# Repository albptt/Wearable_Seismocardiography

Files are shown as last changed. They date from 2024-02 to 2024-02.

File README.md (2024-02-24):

<h1 align="center"> HEA </h1>

<p align="center">
  animated
</p>

   <br> 
   <br> 
   
## Getting Started
### Clone the repository
Run the command on your terminal at the desired location:
```
git clone git@github.com:ltebs-polimi/AY2324_I_Project-6.git
```
### Dependencies
It is recommended to create a virtual environment to run the GUI. This can be done by running on your terminal:
```
python -m virtualenv GUI_venv
```
The latest versions of these libraries should then be installed within the virtual environment:
- ```PyQt5```
- ```numpy```
- ```scipy```
- ```pandas```
- ```openpyxl```
- ```pyqtgraph```
- ```os```
- ```sys```
- ```time```
- ```logging```
- ```struct```
## Filetree
Directories are organized as follows:
```
││├───CASE
│││   └──STL files
│││
││├───GUI
│││   ├──pyqt5_venv
│││   └──GUI.py
│││
││├───PCB
│││   ├──HEA.bdr
│││   └──HEA.sch
│││
││└───PSoC_code
││    ├──Oled-Psoc5
││    └──Stream mode.cydsn
││       │
││       ├───Generated_Source
││       │   └───PSoC5
││       └───TopDesign
││
│└───Validation_Study
│    ├──Output_Measurements
│    └──Plots
│
└───Images

```
   
## Intro
The aim of the present project is to develop a wearable device for the continuous monitoring of the heart rate, using the seismocardiography tecnique. 
  
### Seismocardiography
Continuous cardiac monitoring is necessary for the diagnosis of cardiovascular diseases. Medical emergencies caused by cardiac arrests can be prevented by a continuous cardiac monitoring, which can be easily provided by a wearable device. [^1]

Seismocardiography consists in the extraction of the heart rate value from the measurement of the vibration of the chest caused by the contraction of the heart, the closure of the cardiac valves and the ejection of the blood into the vascolature. [^1]  This term appeared in literature for the first time in the 90's. Vibrations induced by the cardiac activity are mainly correlated to valve closure (heart sounds) and cardiac systole. In particular, seismocardiographic movements at relatively low frequency reflect the recoil forces that results from the contraction of the heart muscle when it ejects blood into the vessels. These forces are responsible for body accelerations in the order of 5 mg. [^2]
  
Failing at reaching the same performances of other well established measurement techniques for the heart rate, seismocardiography didn't find a wide usage in the clinical practice. However, in the last 20 years, thanks to the development brought to the inertial sensors field by MEMS technology, this technique has been at the center of several studies. [^2] Appropriate sensors for seismoardiography are acceleroemeters and IMUs (6 axes accelerometer-gyroscope or 9 axes accelerometer-gyroscope-magnetometer). [^1] Studies present in literature investigated the usage of both single sensors and multiple sensors combined together, and vary in the site of measurement and type of processing utilized. 
  
With the spread of wearable devices and the lowering in their prices, it becomes important to further study the application of cheap and miniaturized sensors to perform biosignal analysis.
Accelerometers and ECG electrodes are common sensors inserted in smart garments such as T-shirts for the monitoring of the athlete performance and smart pajamas for the assessment of the quality of sleep. One of the main objectives in this field is the reduction in the number of the sensors needed to extract the wanted information. Limiting the electronics reduces both the production and the maintenance costs and simplifies the design of such garments. 

Most of the studies present in literature use just one accelerometer as sensor to study the heart rate acquisition in static conditions. Some more recent studies proposed the usage of a second accelerometer to measure the accelerations at the chest level not caused by the cardiac contraction, in order to remove motion artefacts that are superimposed to the heart signal and to make the tecnique effective even in conditions of light movement. [^3]
  
### Heart attack
The proposed solution is a device called "Heart attack" or "HEA" in short. It uses a single 3 axes accelerometer positioned on the chest in contact with the skin, connected through wires to a unit that can be worn on the belt or on the side with a shoulder strap, and that both provides a first interface with the user and manages the communication with a pc. A graphical user interface shows on a pc the result of the measurement and makes the utilizer able to connect and operate with the device. In short, the device records the data relative to the acceleration of the chest of the user and sends it to a pc that has previously been connected to the device throught the appropriate software. The processing of the raw data and the computation of the heart rate value is performed on the pc. Then, the extracted HR value is both sent back to the device, which uses it to manage the peripherals, and displayed on the pc screen both numerically and through a real-time plot. 

The initial solution aimed to incorporate the use of two accelerometers, but during the development process, it was decided to opt for a single accelerometer. This choice yielded satisfactory results while maintaining the simplicity and cost-effectiveness of the device in a hypothetical industrial context.
  
The details of the project are discussed in the following sections:
- [Hardware](#hardware)
- [Firmware](#firmware)
- [Communcation](#communication)
- [Processing](#processing)
- [Graphical user interface](#graphical-user-interface)
- [Acquisition Protocol](#acquisition-protocol) 
- [Clinical validation study](#clinical-validation-study) 
- [Limitations and future developments](#limitations-and-future-developments)

   <br> 
   
## Hardware
### Reference Folder: `PCB`, `Case_3Dprint`
  
HEA is composed by an accelerometer fixed in position on the chest of the user by a band and inserted in a protective shell, and by a central unit installed into a rigid case that can be worn on the belt, thanks to a clip, or on the side thanks to a shoulder strap.  

<br> 

<div align="center">

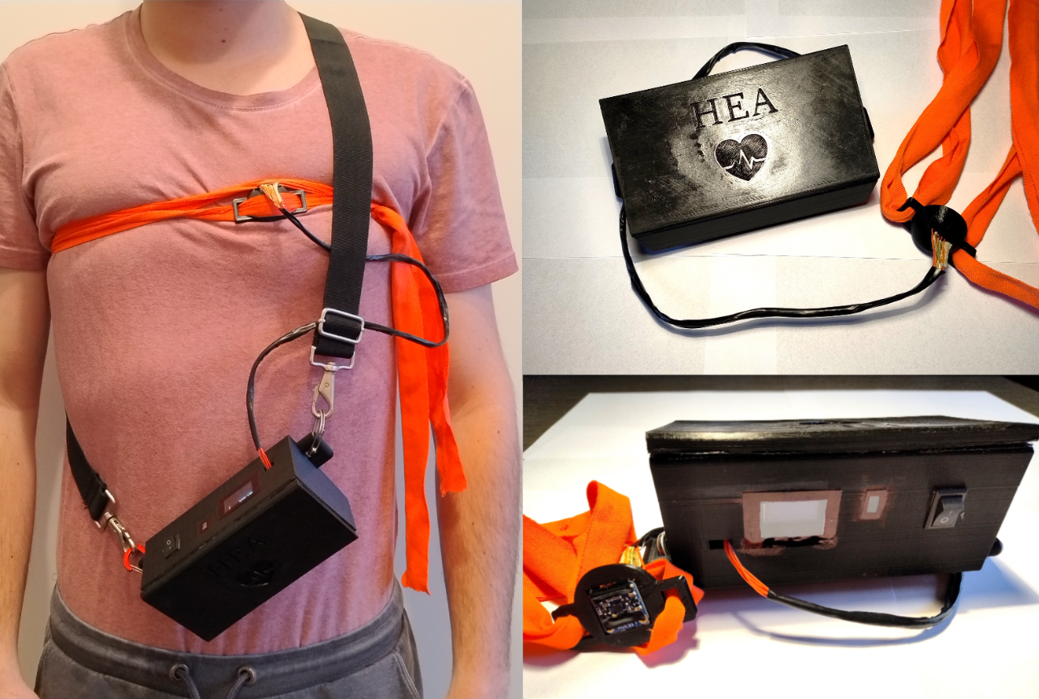
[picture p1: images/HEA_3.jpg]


</div>
  
<br>
  
The electronic circuit has been simulated in breaboard before designing the PCB.   
The electronical components used for the main module are: 
- Psoc 5LP, accelerometer LIS3DH, bluetooth module HC-O6, OLED screen ElectroPeak 0.96'', RBG led, buzzer, 9V alkaline battery, switch, linear voltage regulator LM7805, resistors (220Ω 2x, 330Ω 4x, 1KΩ 4x, 10KΩ 2x), capacitor 100μF.
  
<br>  

<div align="center">

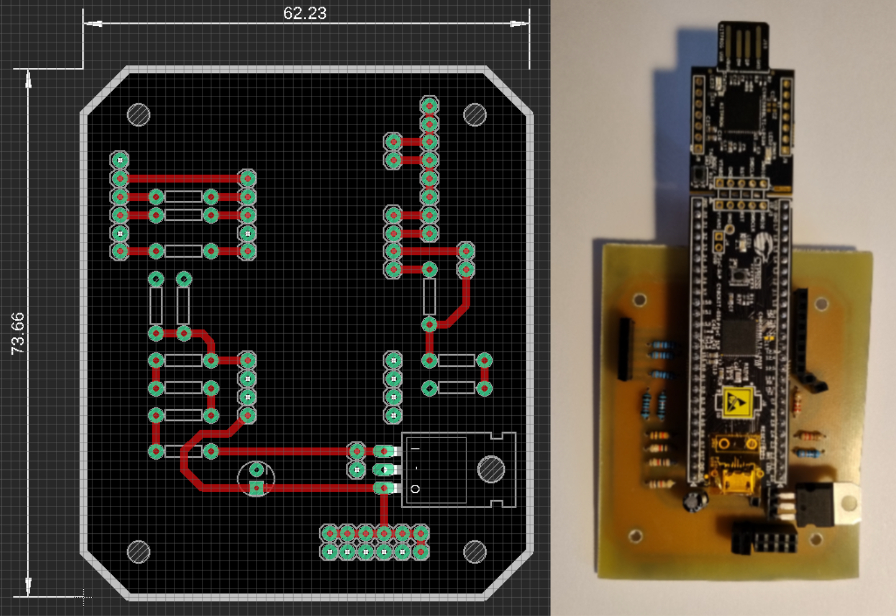
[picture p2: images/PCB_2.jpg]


</div>
  
<br>
  
A reset circuit has been added to the main module in order to automatically reset the microcontroller every time the device is turned on.
The electronical components used for the reset circuit are: 
- Dual Operational Amplifier LMx58 Low-Power, resistors (220Ω 1X, 330Ω 1X, 10KΩ 1x), capacitor 470μF.
  
<br>  

<div align="center">
  
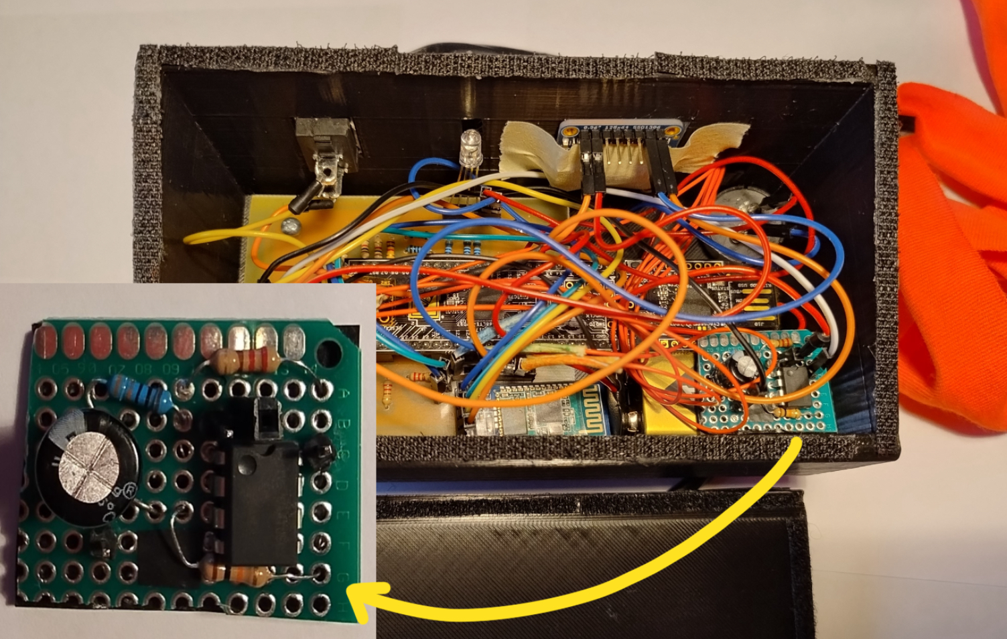
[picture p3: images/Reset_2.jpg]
Reset Circuit


</div>

 <br> 
  
### Hardware functioning discussion:
- The accelerometer and the OLED screen communicate with the microcontroller via I2C, whereas the bluetooth module communicates via UART.
- The accelerometer has also a connection between its interrupt pin and a pin of the microcontroller, so that it can trigger an interrupt when the FIFO register is full. 
- The oled screen shows the name of the device on power on. After 5 seconds it switches to a second window that shows the heart rate value and battery level over time. When the streaming is ongoing, the OLED screen is updated every 5 seconds with the new istantaneous HR value. Every hour the battery level is sampled, this event triggers also an update of the OLED screen to display the updated battery level. 
- The RGB led communicates information about the connection status of the device. If the device is not connected it flashes a red light, if the device is connected but it is not streaming data it emits a stable green light, if the device is connected and it is streaming data it emits a stable blue light. 
- The buzzer can supply information about the state of the battery and about the heart rate value via an alarm. The alarm is triggered when the heart rate value overcomes 120 bpm (which means that the user is suffering tachycardia) or when the battery goes below 5% (a new battery is needed). The alarm lasts 3 seconds, then it is disabled for 30 seconds, after which, if the triggering condition is still present, it will turn on again. 
- The PSOC 5LP and all the peripherals run on 5V, so the 9V of the battery are reduced and stabilized to 5V by the linear voltage regulator. 
- Resistors are used to limit the current running in the RGB led and to reduce the TX signal sent by the microcontroller to the bluetooth module from 5V to 3.3V, to cope with the HC-06 limitations. 
- The 100μF capacitor grants a constant power supply even in case of spikes in the current request of the circuit. 
- A voltage divider is used to reduce the 9V of the battery to 5V in a proportional way, in order to sample such signal with a pin of the microcontroller connected to an ADC and to use it as indication of the battery residual charge.
- The PCB hosts the passive components (capacitor and resistors) and the headers for the pluggable components, providing a compact platform for all the elements.
- The reset circuit generates a 0V signal that lasts approximately 3 seconds when the device is turned on. This signal is generated at the output of a comparator powered between 5V and ground. The non inverting input of the comparator is connected to the positive terminal of a capacitor which is in series to a resitor. As soon as the device is switched on the capacitor starts to charge, when its voltage overcomes 3V (present at the inverting input of the comparator and generated by a voltage divider) the output of the comparator turns from 0V fo approximately 3.6V, ending the 0V signal. This 0V-2s pulse is sent to the reset pin of the microcontroller. 

### 3D printed case design discussion:
- The 3D printed case is meant to contain the PCB with all the peripherals except for the accelerometer, which is instead encapsulated in a protective shell and worn on the torso, fixed in position by an elastic band. Some windows in the upper panel of the case grant the visibility of the OLED screen and of the RGB led, provide a passage for the accelerometer cables and host the switch. The case can be worn on the belt thanks to a clip or on the side via a shoulder strap. The PCB is screwed inside the case whereas all the other components are glued in position. The cover can be easily removed and placed back in position thanks to velcro straps.

<div align="center">

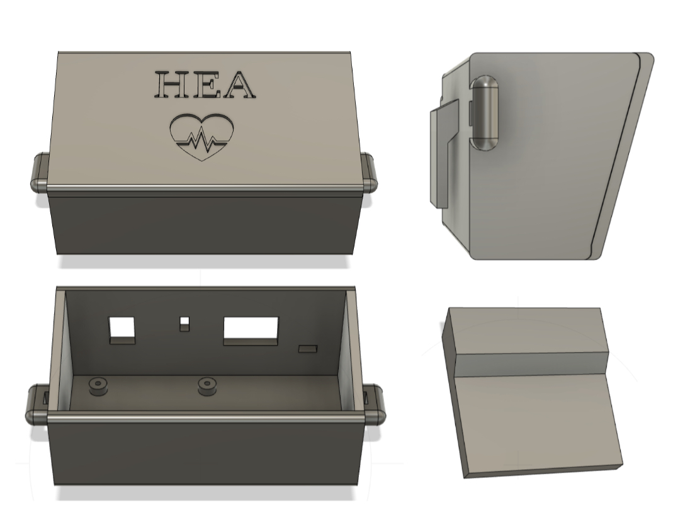
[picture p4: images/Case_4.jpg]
Case

  
</div>

<div align="center">

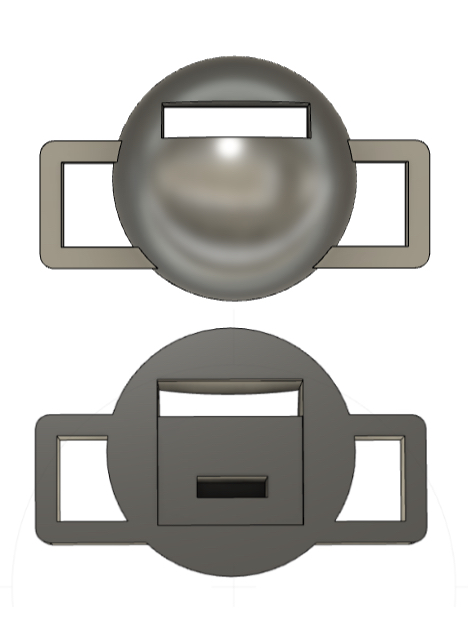
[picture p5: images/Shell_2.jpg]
Shell


</div>

   <br> 
   
## Firmware
### Reference Folder: `PSoC_code`
The initial configuration state of each peripheral is stored within the EEPROM memory of the PSoC5 device, these are read at each power-on. Namely, the information stored concerns:
- The sentence to be displayed on the OLED screen at startup
- The color shown by the RBG led at startup
- The initial off state of the Buzzer
- The resolution in bit and the full scale in g of the accelerometer data

During normal running conditions, the EEPROM writing occurs only upon receiving a new bit resolution configuration or full-scale configuration, from the GUI, or when the device enters low-power mode, to ensure that the new settings are persistent upon the next power-on. An if statement on the macro `WRITE_EEPROM` is instead implemented for the first EEPROM programming, once done, the macro is set to False.

<br> 

<div align="center">

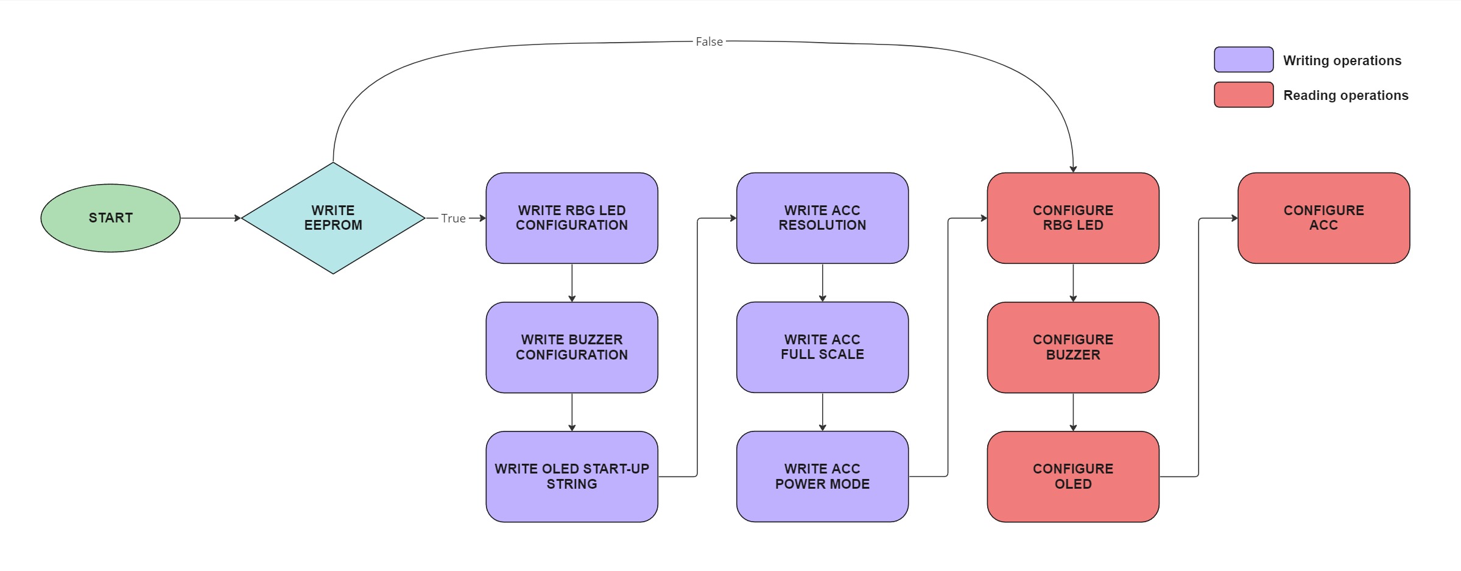
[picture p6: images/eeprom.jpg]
Eeprom


</div>
  
<br>

Recommended settings for HR measurement are: 10bit resolution and +2/-2g full scale. Entering low-power mode implies reducing the resolution to 8bit.
  
The OLED screen serves the purpose to provide an additional interface for the user and its management relies on an [open source library](https://github.com/NRDaza/Oled-Psoc5). When the device is powered on, the OLED screen shows the name of the device "Heart Attack" for 5 seconds, and then it shows the main window. The main window is composed by the acronym "HEA" at the top, followed by the indication on the current heart rate and by the residual battery charge. The heart rate corresponds to the instantaneous heart rate shown in the GUI and is updated every 5 seconds. On the other hand, the battery is sampled for the first time 5 seconds after powering on, then it is sampled again and updated on the OLED screen every hour. If the battery level is under 5% the sound alarm by the buzzer is turned on for 3 seconds and the device automatically enters in low power mode. The sound alarm is also activated if the measured heart rate exceeds 120bpm, as the device is intended for stationary use. After the 3 seconds, the buzzer undergoes a refractory period of 30 seconds before re-entering the triggerable mode.

The RBG LED is meant to signal the connection status of the device. Initially, while HEA is not yet paired with the laptop, the LED will blink in RED driven by a PWM signal with a period of 1 second and duty cycle of 50%. Successful pairing is then flagged via a fixed green light, while during data streaming a fixed blue light is shown.

<div align="center">

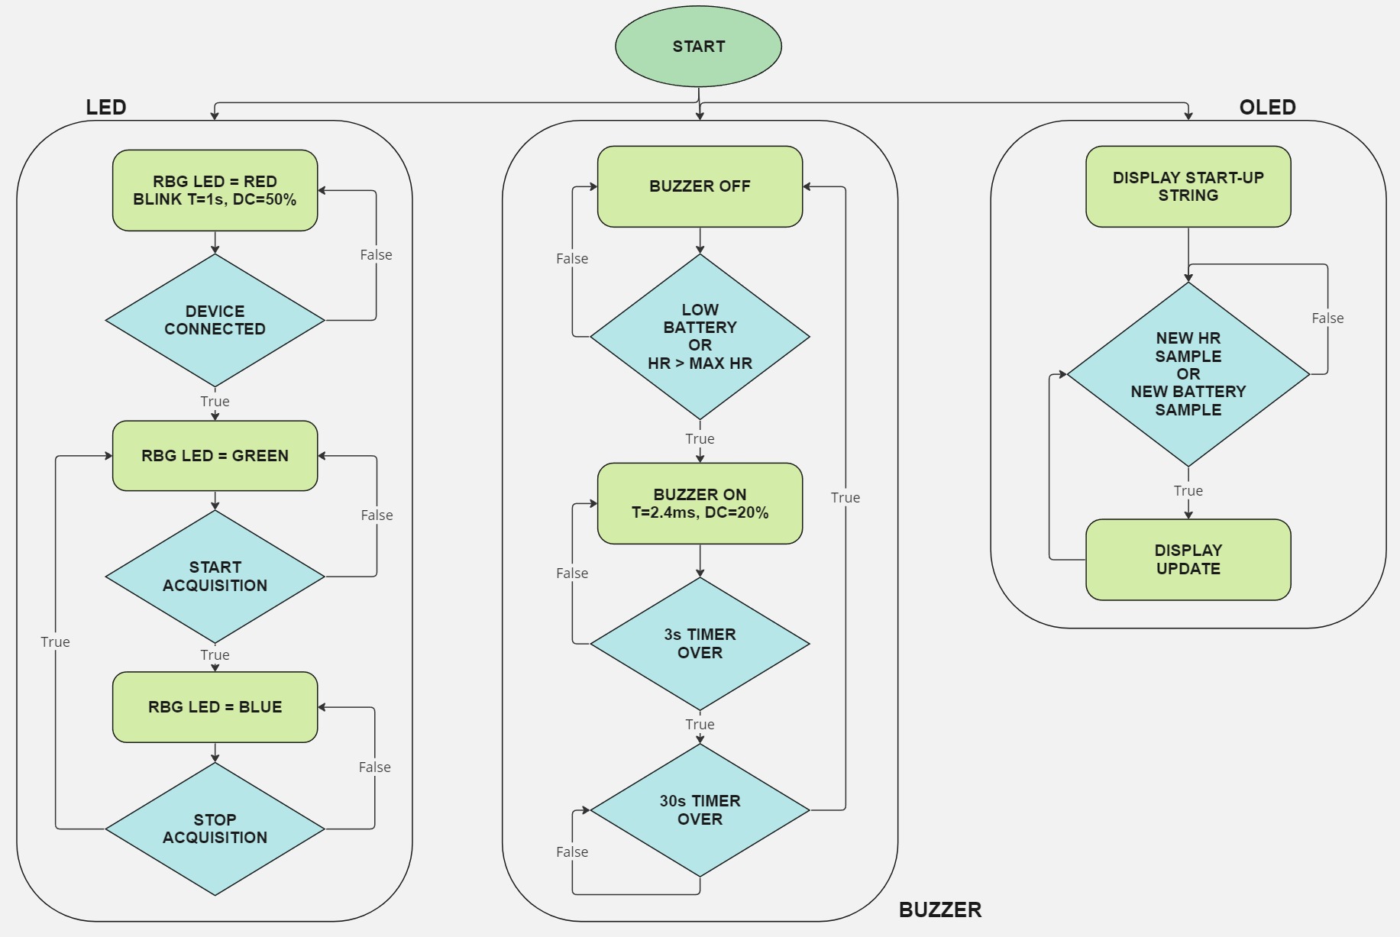
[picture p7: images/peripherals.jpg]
Peripherals


</div>

Accelerometer reading is performed exploiting the integrated 32-level FIFO register. The FIFO is filled at a 50Hz sampling frequency. As the last level is filled, the `OVRN` bit in the `FIFO_SRC_REG` is set HIGH triggering an interrupt service routine. Within the ISR, initial attempts at recovering the data consisted in reading each FIFO level one at a time and reconstructing the acceleration along each axis, before transmitting it via UART protocol to the GUI. Being implemented while using FIFO mode, this approach was faulty and resulted in hundreds of acceleration samples being lost, due to the fact that data collection is stopped until all registers are read and a different mode is selected. 

<br> 

<div align="center">

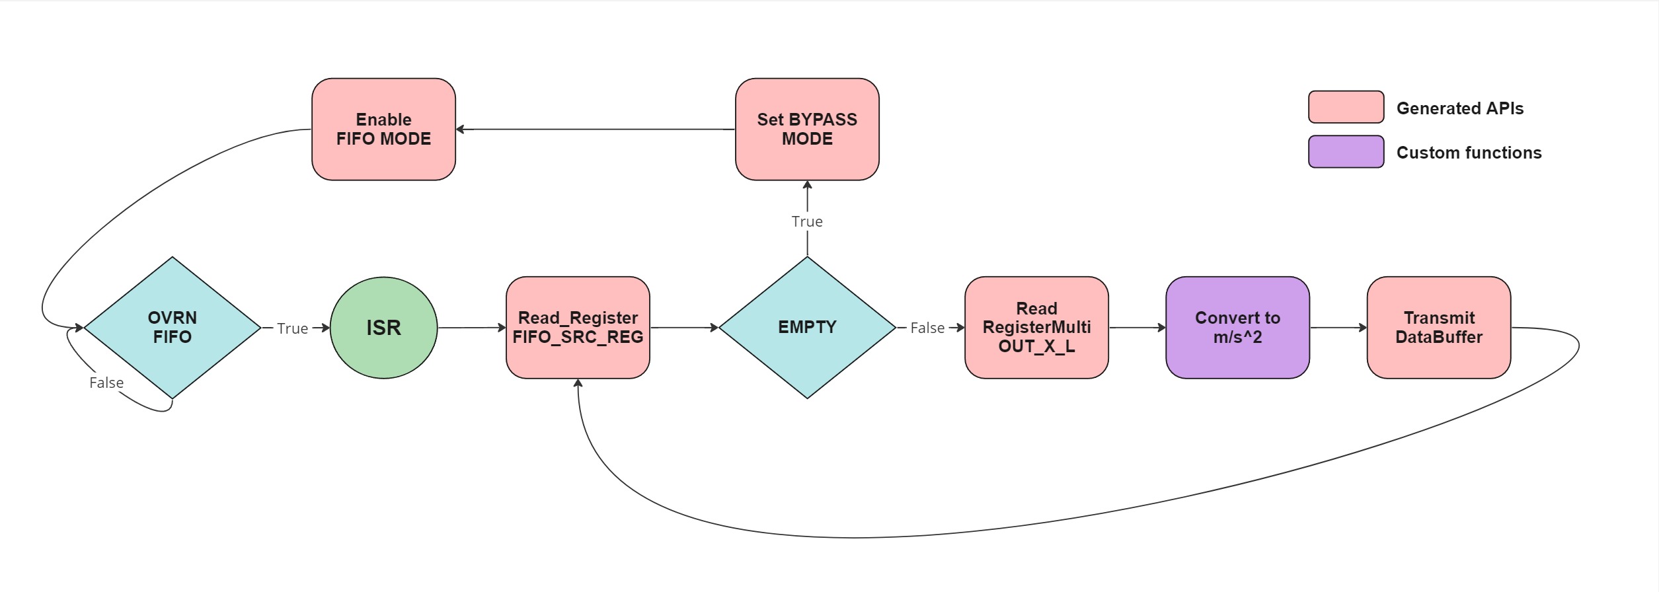
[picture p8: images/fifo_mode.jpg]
Fifo Mode


</div>
  
<br>

For this reason, Stream mode was implemented, in this case when the buffer is full, the FIFO index restarts from the beginning and older data is replaced by the current. To avoid the risk of overwriting samples, the reading procedure was sped up by shrinking the ISR to perform the reading of all the 192 bytes at once and transmitting them raw.

<br> 

<div align="center">

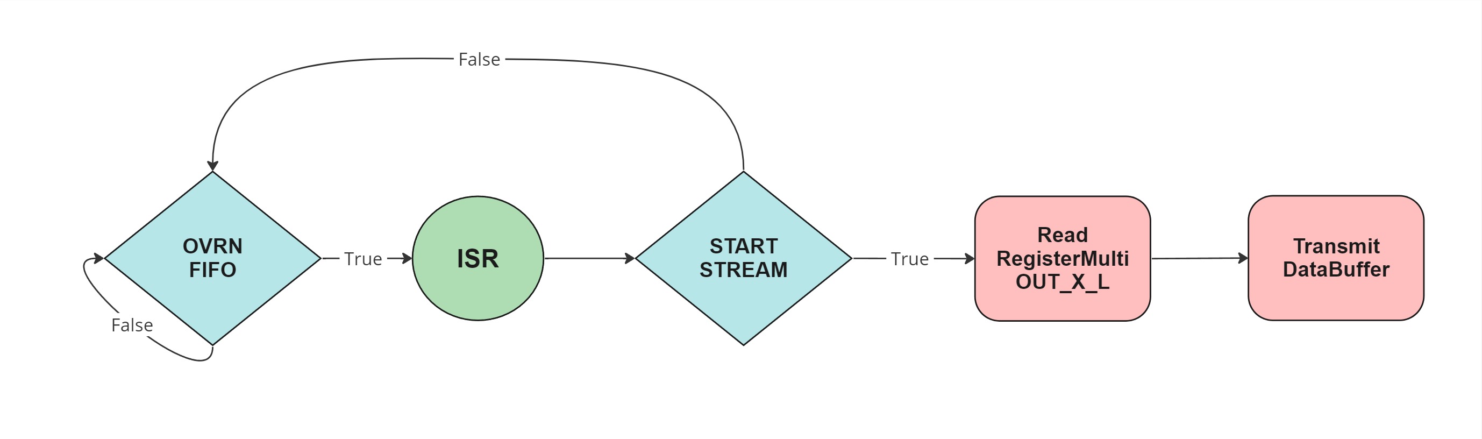
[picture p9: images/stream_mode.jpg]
Stream Mode


</div>
  
<br>

   <br> 
   
## Communication
### Reference Folder: `PSoC_code`, `GUI`
The visualization on the GUI of the acquired data is possible thanks to the serial communication that connects the microcontroller and the GUI interface via Bluetooth.
The port is automatically detected by clicking the button "Connect" (which triggers the sending of character "v") and waiting for the response from the microcontroller: if the line "Go $$$" is correctly received, then the COM port is open and data streaming can occur. Sending a character from keyboard makes sure that only the wanted device is called, which in this case is redundant dealing with only one device, but it increases the robustness of the application. 

Once the line is received, the GUI is ready to receive the current settings saved in the EEPROM memory of the device; this is done by sending via software the letter "k", whose purpose from the PSoC side is to trigger a case devolved to sending the bit resolution and the g resolution values.

<br> 

<div align="center">

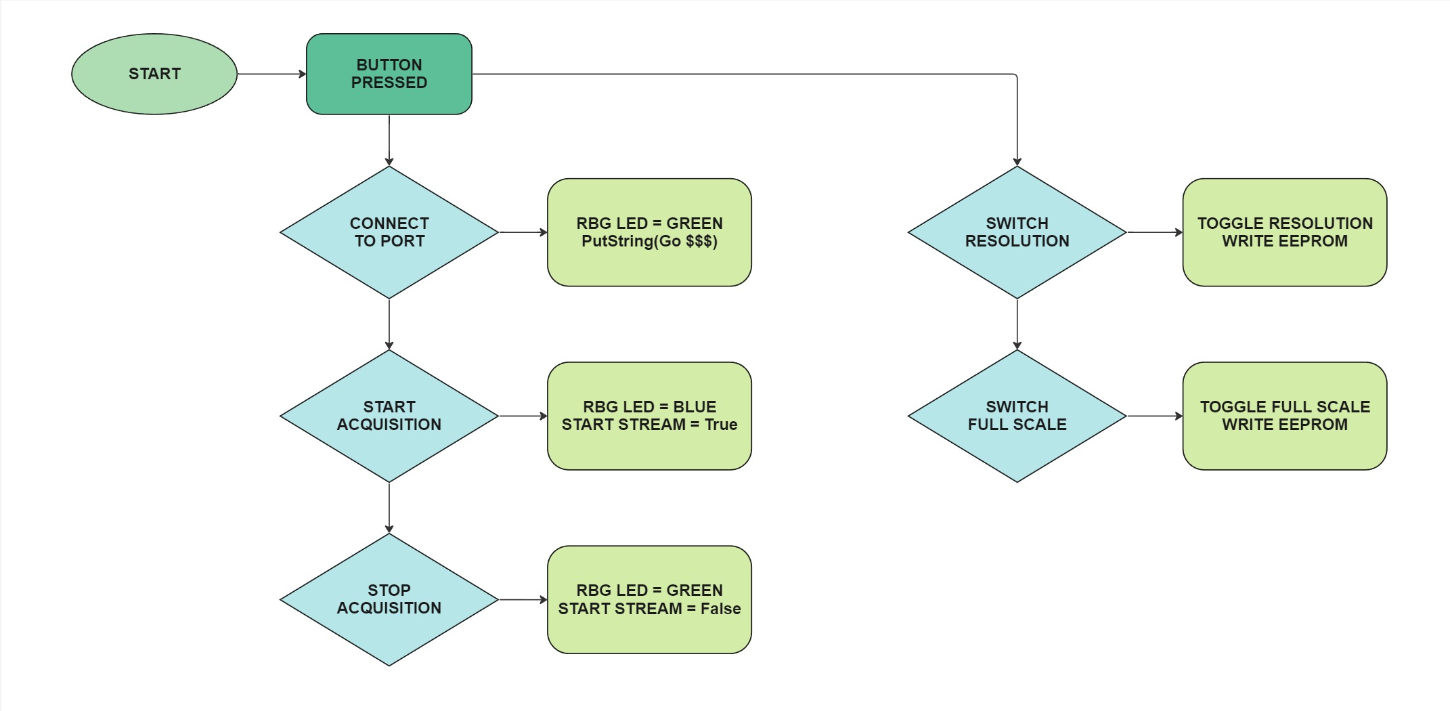
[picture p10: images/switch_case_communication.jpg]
SwitchCase


</div>
  
<br>

If the status of the device is connected, then data streaming can occur, depending on the character (or the shortcut) that the user presses: if "Start acquisition" (or CTRL+b), streaming starts, if "Stop acquisition" (or CTRL+f), streaming stops. Of note, the shortcut to stop streaming was changed from CTRL+s to CTRL+f, because CTRL+s was then used to implement data downloading on an excel file (see section GUI for more details). However, the CTRL+f shortcut still enables the sending of the "s" character, which is the one the PSoC recognizes to stop data streaming. 
The management of the possible variables involved in the bidirectional communication between PSoC and GUI is assolved through a "while" cycle, which is active whenever the condition of connected device and correct string received are satisfied. The "while" comprehends a number of "if" conditions equal to the number of possible buffers, distinguishable thanks to their headers, and has a frequency equal to the accelerometer ISR triggering; therefore, at every iteration of the while loop, 32 samples of acceleration are acquired. The acquisition comprehends unpacking the 192 bytes, converting them properly according to the `BIT_RESOLUTION` and `G_RESOLUTION` global variables, and saving them in variables that can be exploited to update the graph. 

The "if" condition involved in data reading is responsible of triggering the processing flag, which starts the processing chain that will be explained in the following section. Among the other steps, the dispatch of the heart rate value that will be streamed on the OLED, is also included.  

The other "if" conditions are devoted to acquire respectively: the eventual data from the second accelerometer, the g resolution, assigned here to `G_RESOLUTION`, the bit resolution, assigned here to `BIT_RESOLUTION`, and the power mode, which allows to set the `LOW_BATTERY` global, and to show an appropriate warning to the user to suggest the substitution of the battery. The `BIT_RESOLUTION` value can toggle between 8 and 10 bits, the `G_RESOLUTION` value can toggle between 2 and 4 g; these values are consistent with the modality in which the accelerometer is used - using its built-in FIFO - and with the typical value ranges of the specific application - seismocardiography. Of note, these values can be set by the user throughout the acquisition through appropriate buttons (which will be described in section GUI); nevertheless, there's a mismatch of 32 samples between the updating on the software and on the firmware, causing that small portion to have inaccurate values; this can be signaled to the user through a proper warning. 

<br> 

<div align="center">

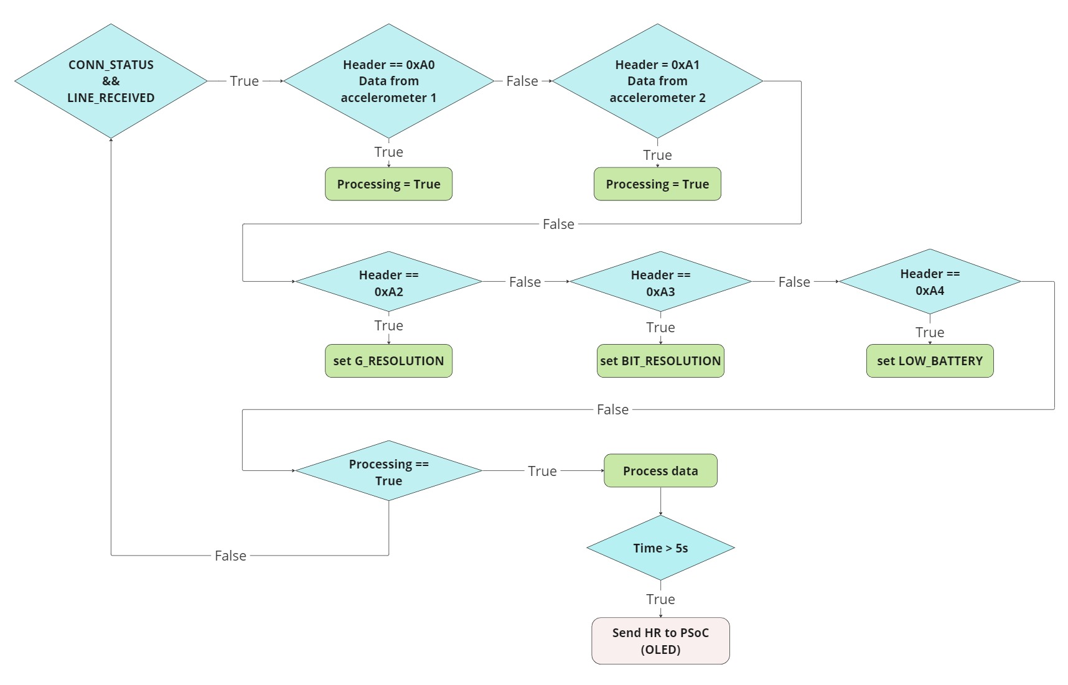
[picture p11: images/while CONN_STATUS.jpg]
Conn_Status


</div>
  
<br>

   <br> 
   
## Processing
### Reference Folder: `GUI`
Different processing strategies have been investigated. Among the ones showing promissing results, the choosen one shows good concordance with the gold standard device used as reference for the wider HR interval. 
The processing of the signal is composed by the following steps: 
  
- A vector containing 1500 samples (corresponding to 30 seconds since the sampling frequency is 50Hz) of the acceleration on the Z axes is the input to the processing chain.
- Rectification is applied to the raw data vector.
- A Butterworth high pass filter of the fourth order with cut off frequency of 18Hz extracts the cardiac sounds from the overall chest perpendicular acceleration signal. [^2]
- The first 100 samples of the resulting vector are removed to clean the distortion introuced by the filter, the remaining samples are rectified.
- The processed signal is normalized with the z-score and then rectified.
- A threshold equal to the 80% of the variance of the energy of the final signal is computed. [^1]
- The function find peaks of the scipy library extracts the peaks showing the closure of the aortic valve (cardiac event that causes the maximal vibration of the chest).
- The HR value is computed as the mean of the time intervals between the detected peaks.
  
<br> 

<div align="center">

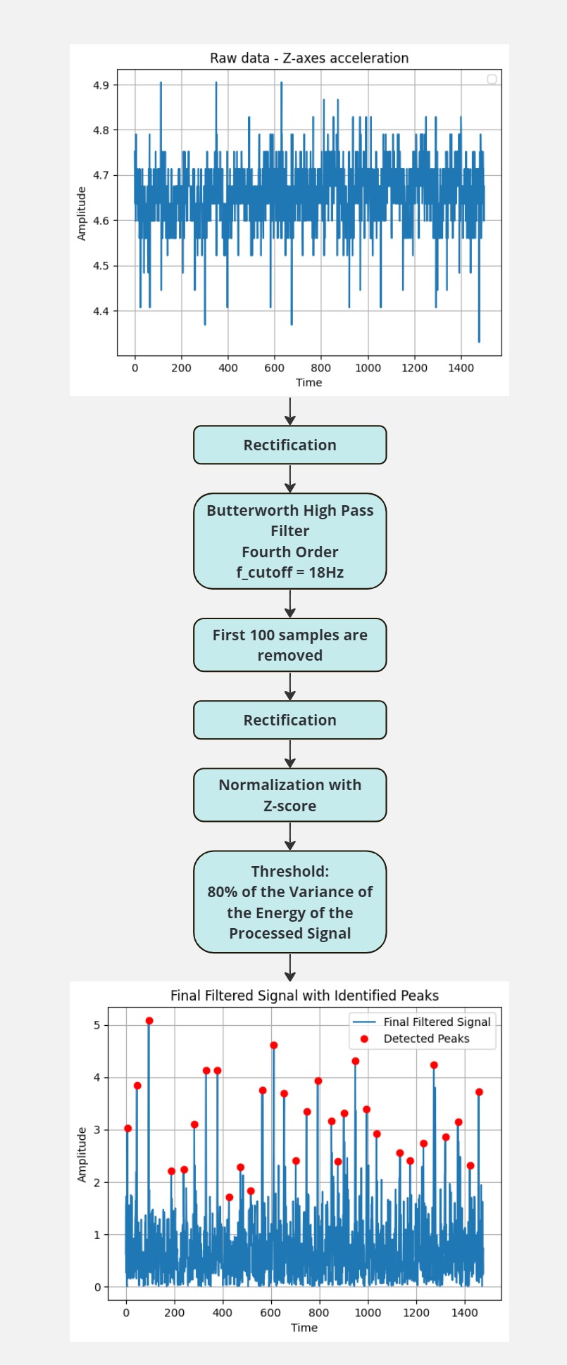
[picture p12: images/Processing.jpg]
Processing


</div>
  
<br>

- This processing is applied every time a new group of 32 samples is delivered to the pc (approximately every 0.64 seconds).
- The value of HR istantaneous is updated every 5 seconds and it is computed as the mean of all the HR values computed in the 5 seconds window prior to the update.
- The value of HR mean is updated every 60 seconds and it is computed as the mean of all the HR values computed in the 60 seconds window prior to the update.
  
It is worth mentioning also the following processing which applies a very different approach and that shows good performances in the range 60bpm-80bpm:
- A vector containing 1500 samples of the acceleration on the Z axes is the input to the processing chain.
- The absolute value of such raw data is first denoised by using a Savitzky-Golay filter. In particular this filter extracts the respiratory signal from the raw data, so by subtracting it from the raw data we can already eliminate a big noise component. [^1]
- A Butterworth fitler of the fourth order between 0.6Hz and 3.6Hz eliminates the freqeuncy components that do not contain the heart rate signal. 
- The processed signal is normalized with the z-score. 
- Thanks to a threshold equal to the 80% of the standard deviation of the analyzed signal it is possible to determine the peaks linked to the valve activity. 
- Once the time istants associated with such peaks are extracted, the heart rate value can be computed from the time interval between peaks. 

   <br> 
   
## Graphical user interface
### Reference Folder: `GUI`
The graphical user interface incorporates all the features necessary to communicate with the device in one window.

To ease the connection with the device, the GUI is equipped with a scroll down menu and two buttons: "Scan" and "Connect to port {}". The box contains the list of serial ports that were found after the serial scan at the start of the GUI. In case it was started before the Bluetooth connection was enabled, the button Scan allows to call the serial scan again, thanks to a signal emitted by the SerialScanner class, and to update the list of ports in the combo box. Finally, the Connect button allows the actual connection with the device, only if the COM port is correct and the device sent the correct string. 

The graphical interface includes a dynamic graph window facilitating the visualization of both raw and processed data. 
The plotting commences after an initial 45-second calibration phase initiated by pressing the Start button. Utilizing the PyQtGraph Python library, the plot displays multiples of 32 samples. 
The "ready" and "ready processing" flags in the serial worker are set to 1 upon the availability of new samples. 
Every second, the Main Window, driven by a timer, checks these flags. If they equal one, the acquired samples are passed to the relevant function in the Main Window, plotted, 
and then the flags are reset to 0 until new samples are acquired. 
A button beneath the graph allows users to toggle between visualizing raw and processed data. Additionally, two buttons enable users to select the background color of the plot (light or dark mode) and clear the graph view.

On the right side of the GUI, editable lines allow users to input personal data about subjects. These data are utilized to create filenames when saving files (see details below).

Two LCD displays provide real-time visualization of instantaneous HR and mean HR. The instantaneous HR is updated every 5 seconds to enhance stability in the displayed value. The mean HR is updated every minute, calculated as the average of the last 12 samples of instantaneous HR shown.

The File menu bar encompasses three actions. The first two actions, "Start Acquisition" and "Stop Acquisition", have been previously discussed in the Communication section. 
The third action, "Save Data," enables users to contemporaneously save two Excel files: one containing raw data values and the other containing instantaneous HR values. 
Filenames are generated based on the user-entered data in the editable lines, structured as follows:
- Raw_data = '{name}_{surname}_{age}.xlsx'
- Instantaneous_HR = f'{name}_{surname}_{age}_HR.xlsx'

These files are intended for more robust offline analysis.

The Settings menu bar offers two actions allowing users to select the desired bit resolution and full scale by toggling between the two available values. 
The current values are continuously displayed on the screen.

Any event from the GUI raising an error is manifested to the user in the form of message boxes with informative text. 

   <br> 

## Acquisition Protocol

Before each acquisition, a protocol was formulated and followed to ensure consistency in results, minimizing possible errors and biases that may compromise the quality of data.

The protocol is articulated in the following steps:

__1. Preparation__: 
- Clean the skin where the accelerometer will be attached to ensure proper adhesion and minimize interference from sweat.
- Choose an appropriate location for attachment based on the anatomical characteristics of the subject’s chest.
- If it's possible to feel the heartbeat by lightly touching the protective shell encapsulating the accelerometer, then the positioning is valid.
- Ensure the device is fully charged or has sufficient battery life to support the duration of data collection.
 
__2. Attachment__:
- Securely affix the accelerometer device to the chosen location with the help of another person.
- Double check the fit to ensure the device is sufficiently but not overly tight to avoid discomfort and allow for normal breathing.

__3. Subject Positioning__:

Three conditions were tested:

- __Seated__: the subject is instructed to sit comfortably with their back supported and feet flat on the ground. Arms are resting on a table and the pulse-oximeter to monitor the reference heart rate is applied to the right index finger. HEA is placed on the table as well in front of the subject, cables are lifted to prevent artifacts due to their breathing-induced dragging on the table.
- __Upright__: the subject is standing straight with minimal movement. Again the pulse-oximeter is applied to the right index finger while the hand is resting on a flat surface. HEA is worn in the belt-like fashion ensuring that cables are not constrained by any strap.
- __Lying down__: the subject lies on an even surface in supine position, while the pulse-oximeter is applied to the right index finger. HEA is placed on the subject’s right side with cables passing over the respective arm.
  
__4. Data collection__: 

Once the previous steps are correctly performed and the subject is ready, data streaming from the device is started. Each acquisition was obtained for a duration of 10 minutes and data was collected every 5 seconds, as the OLED display of HEA is updated, or up to the acquisition of 100 samples. 

   <br> 
   
## Clinical validation study
### Reference Folder: `Statistical_Analysis`
In order to assess the quality of the device a small clinical validation study has been performed. 
To assess the applicability of a measuring instrument in a clinical context, it is necessary to evaluate its validity and reliability (intra- and inter-operator). In cases where such an instrument operates without the intervention of an operator, the validity of its measurements remains the major determining parameter.
Therefore, it is essential to compare the new measuring instrument under analysis with one that is already certified and validated, considered the gold standard. If it is proven that the distributions of measurements from the two devices are strongly correlated, and this assertion holds statistical significance, then the validity of the measurements of the new measuring instrument has been demonstrated.
The clinically validated measurement system used as gold standard in the present study is a Pulse Oximeter A340 produced by Aeon Technology.

The first step involves plotting the coupled measurements obtained from both the new instrument and the gold standard reference. From those plots it is possible to qualitatively analyze the trends of the measurements and the presence of possible biases.
Then some basic statistics are computed (error = Hea measurement - Pulse Oximeter measurement): mean error, mean absolute error, maximum absolute error, minimum absolute error, standard deviation of the absolute error, root mean square error. [^1]
The interpretation of those statistics is straight forward: the lower the better. In the current project a deviation of ±5bpm from the measurements of the gold standard device is considered acceptable.

To verify the correlation between the two data distributions, it is first necessary to determine whether these distributions are normal or not. If both distributions are normal, then the Pearson coefficient is used; otherwise, the Spearman rank correlation coefficient is employed. [^4] The normality of data in the case of small sample sizes is assessed using the Shapiro-Wilk test. [^5]
Both quantitative analyses described above have a qualitative counterpart consisting of interpretable graphs: QQ-plot for normality verification and Bland-Altman plot for correlation verification, with the limits of agreement computed as 1.96 * standard deviation of the differences. [^6]
If the calculated validity coefficient exceeds the threshold of 0.7, then the new measuring instrument is considered valid.
An interpretation commonly used for the correlation coefficient is: 0.90 to 1.00 = excellent, 0.70 to 0.89 = good, 0.50 to 0.69 = moderate, 0.30 to 0.49 = low, <0.30 negligible. [^7]
The minimum number of data points for each distribution should be 20 (significance level 0.05 (alpha), power 0.20 (beta), assuming a moderate correlation between measurements). [^8]

Several acquisitions have been performed during the course of the project on different partecipants that varied for gender and chest anatomy. Those acquisitions have been taken under a multitude of settings: static, with slight motion, with wide movements, seated, standing, laying down. Also different sensor positionings over the chest of the patient have been experimented. The various testing conditions determine the bpm range that is explored during the acquisition. Those measurements have been used to reject inadequate processing methods or sensor positionings. In the end, the choosen processing algorithm described in the section "Processing" has been analysed through six acquisitions perfomed on the same subject with the following settings: two seated, two standing, two laying down, all in static conditions and at rest. The acquisition protocol followed is descrived in the section "Acquisition Protocol". 

The following table shows the results of the statistical analysis of the processing algorytm currently implementend in the device. 

<br> 

<div align="center">

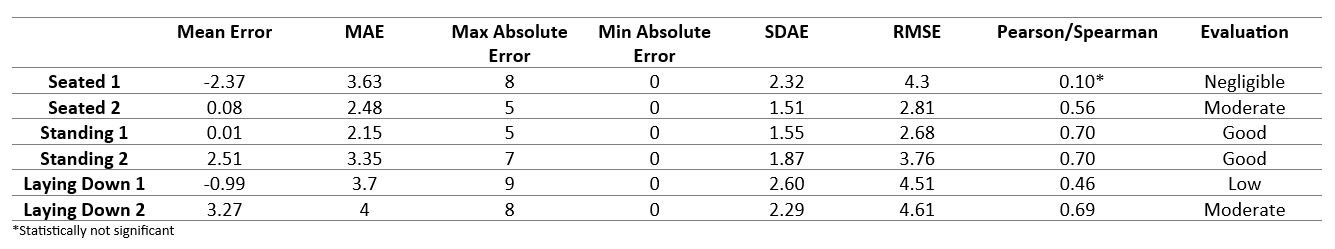
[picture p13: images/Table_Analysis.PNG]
Table_Analysis


</div>
  
<br>

Mean error, MAE, RMSE show results all below the 5bpm target under all three of the different measurements conditions. The correlation has in the end always been computed through the Spearman rank correlation coefficient since the data recorded by the Pulse Oximeter always resulted not normal. Good correlation results are obtained only in the standing position, while in the laying down position and in the seated position not only the results of the coefficient are too low to determine a strong correlation, but they also vary significantly between the two acquisitions. 

From the analysis of the plots below we can see that the high correlation highlighted in the standing acquisitions is linked to the capability of HEA in correctly following the big variations of the heart rate over time, like for example when this one increases or decreases in a continuous way from 75bpm to 85bpm in the "standing" acquisitions. It is also possible to link the worse results got in the other two measurement conditions to the incapability of HEA in showing a stable heart rate value when its variations are in a more limited range, as can be seen both in the "seated" and in the "lying down" acquisitions.

<br> 

<div align="center">

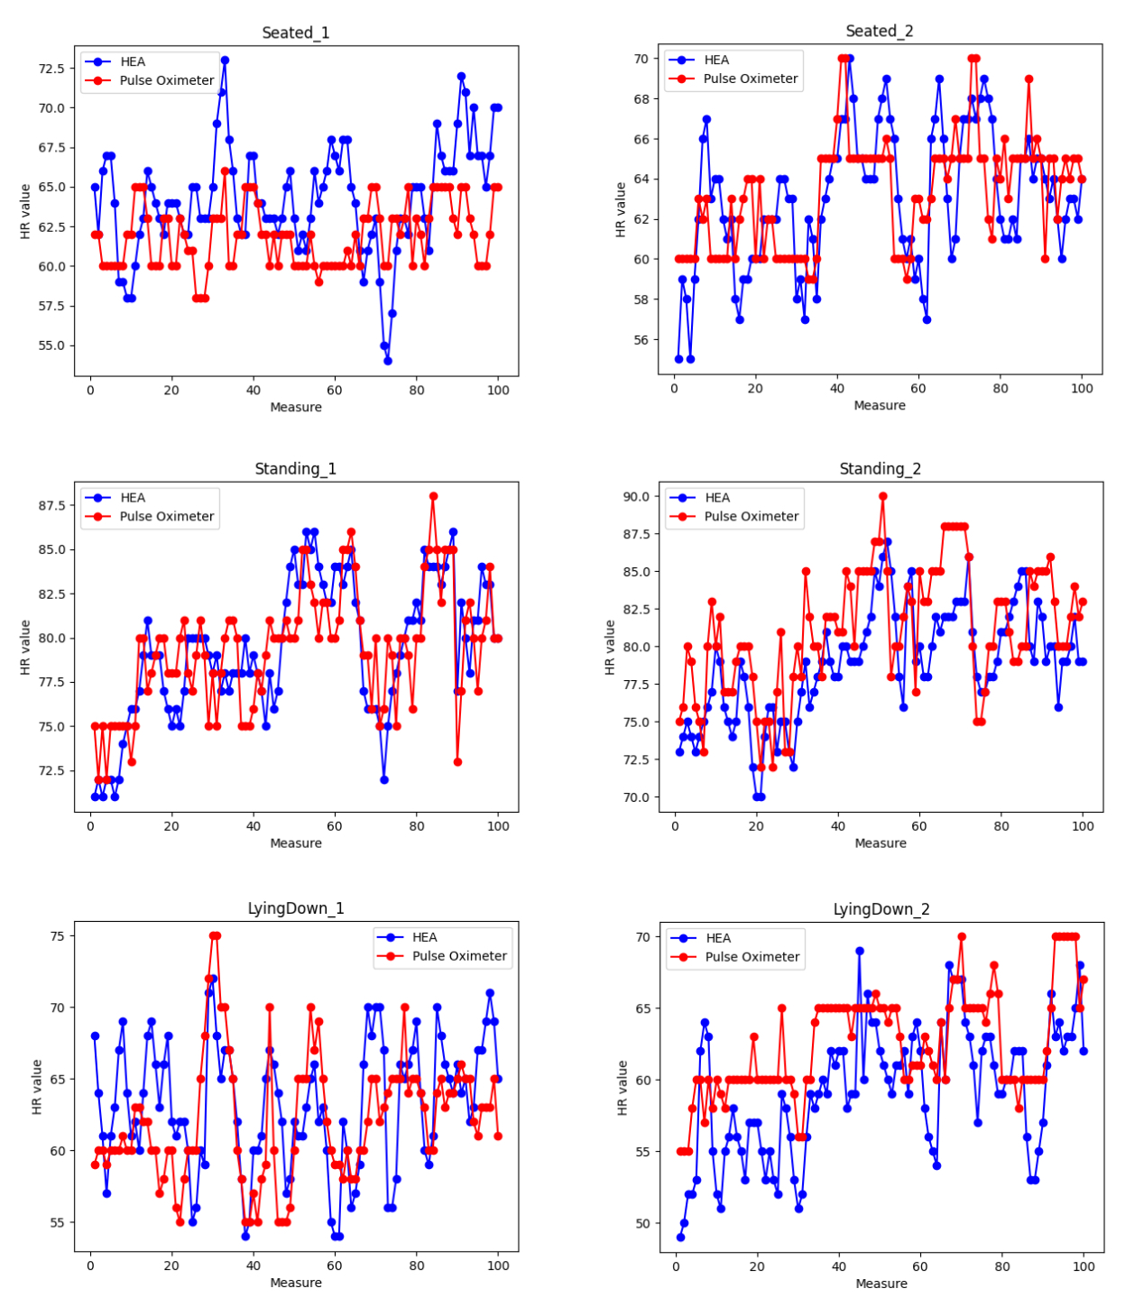
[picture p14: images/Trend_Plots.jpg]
Trend_Plots


</div>
  
<br>

The Bland-Altman plots show no bias in all the measurements sets with the exception of the first seated axquisition, where for lower HR values HEA tents to underestimate the recorded value. This limitation of the device should be further investigated through more acquisitions. 

<br> 

<div align="center">

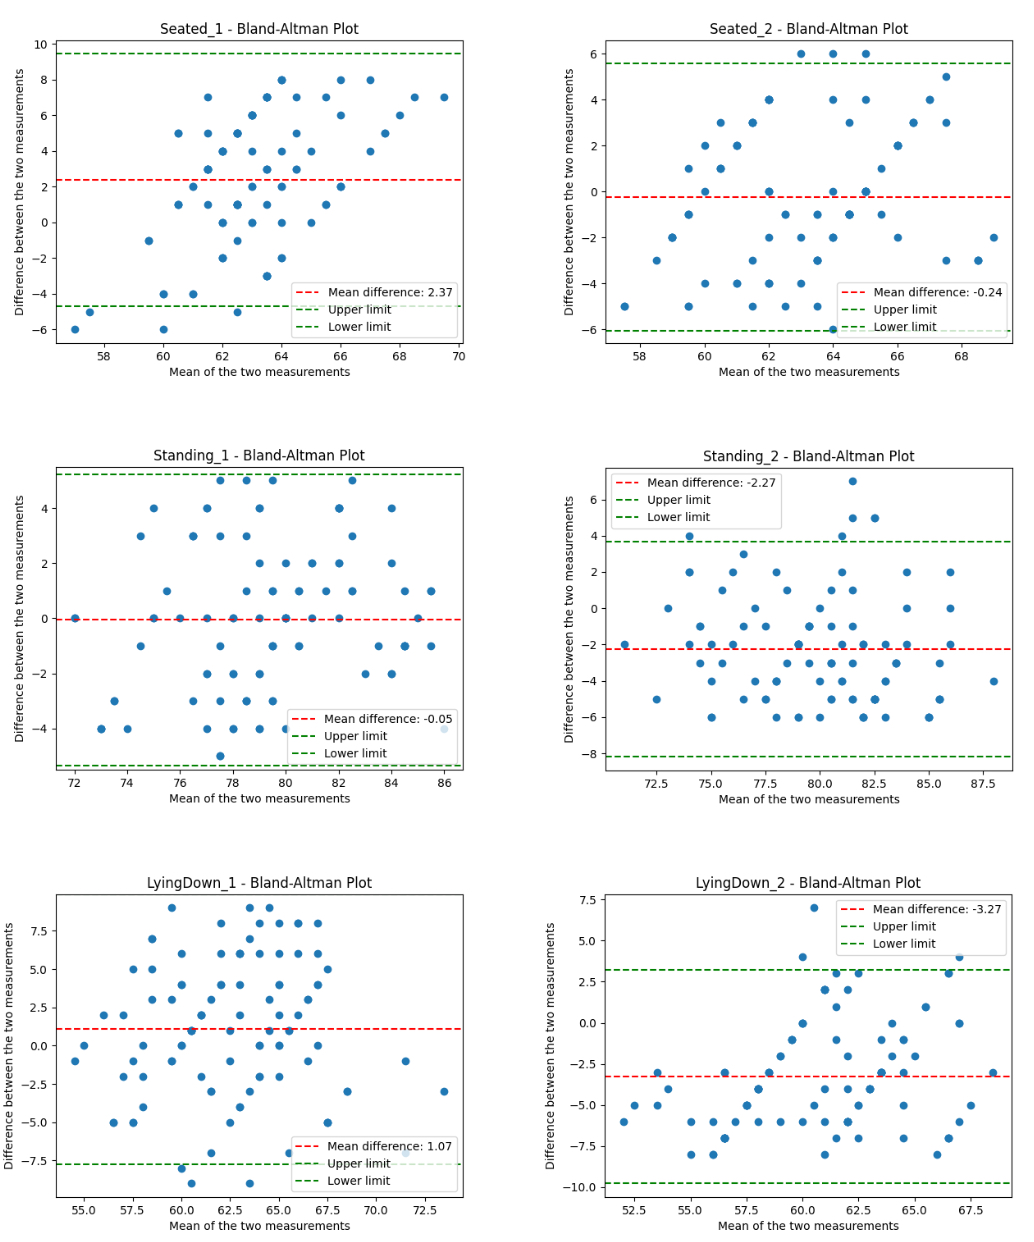
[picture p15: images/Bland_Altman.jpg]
Bland_Altman


</div>
  
<br>

In conclusion, on one hand the results are promising since the computed errors are all below the target error of ±5bpm, on the other hand a more in-depth statistical analysis would be required to assess correctly the correlation between the measurements of the two devices. This would consist in the application of the same approach described in the current chapter, but on a wider database, containing measurements made on a bigger cohort of participants and under a wider range of measurement conditions. 

<br>

## Limitations and future developments

Two main challenges have been identified for the device, the primary being the limited cohort size of partecipants on which the device has been tested, and the second being the requirement of the stillness of the subject to properly estimate heart rate. 

If by testing the device on a wider population the results obtained are subject dependent, a possible solution may involve tailoring the processing algorithms based on individual subject characteristics such as height, weight, age, and sex. By incorporating these variables into the processing framework, the device can potentially yield more accurate and reliable heart rate measurements across a diverse range of users.

To address the second issue, we propose the integration of two accelerometers to enable motion compensation. This approach aims to mitigate the impact of movement on heart rate estimation, thereby enhancing the device's performance in dynamic scenarios.

In conclusion, we believe that the potential solutions identified will improve the device's overall functionality leading to the possibility of integrating it into sensorized garments for everyday monitoring purposes.

*** 

## Authors

- matteo2.mentasti@mail.polimi.it
- alberto.pettenella@mail.polimi.it
- raffaella.salama@mail.polimi.it
- francesca.vacca@mail.polimi.it

<br>

## References
[^1]: H. Lee, H. Lee, and M. Whang, “An enhanced method to estimate heart rate from seismocardiography via ensemble averaging of body movements at six degrees of freedom,” Sensors (Switzerland), vol. 18, no. 1, pp. 1–12, 2018, doi: 10.3390/s18010238.
[^2]: M. Castiglioni, P; Faini, A; Parati, G; Di Rienzo, “Wearable seismocardiography. - MEDLINE® - ProQuest,” pp. 3954–3957, 2007, [Online]. Available: http://search.proquest.com.zorac.aub.aau.dk/medline/docview/68521306/DE9C4DD26AC74FADPQ/3?accountid=8144.
[^3]: L. Luu and A. Dinh, “Artifact noise removal techniques on seismocardiogram using two tri-axial accelerometers,” Sensors (Switzerland), vol. 18, no. 4, 2018, doi: 10.3390/s18041067.
[^4]: Pozzolo P. Coefficiente di correlazione lineare r di Pearson. Published 2020. Accessed June 28, 2022. 
https://paolapozzolo.it/coefficiente-correlazione-statistica-pearson/ 
[^5]: Pozzolo P. La distribuzione normale spiegata semplice. Published 2020. Accessed June 28, 2022. 
https://paolapozzolo.it/distribuzione-normale/ 
[^6]: F. Jacobs, J. Scheerhoorn, E. Mestrom, J. van der Stam, R. Arthur Bouwman, and S. Nienhuijs, “Reliability of heart rate and respiration rate measurements with a wireless accelerometer in postbariatric recovery,” PLoS One, vol. 16, no. 4 April 2021, 2021, doi: 10.1371/journal.pone.0247903.
[^7]: M. M. Mukaka, “Correlation coefficient and its use,” Malawi Med. J., vol. 24, no. September, pp. 69–71, 2012.
[^8]: M. Parati et al., “Video-based Goniometer Applications for Measuring Knee Joint Angles during Walking in Neurological Patients: A Validity, Reliability and Usability Study,” Sensors, vol. 23, no. 4, 2023, doi: 10.3390/s23042232.

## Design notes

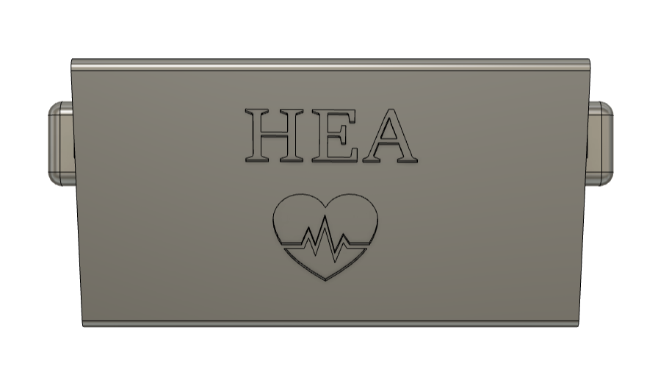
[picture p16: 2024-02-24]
images/Case1.PNG

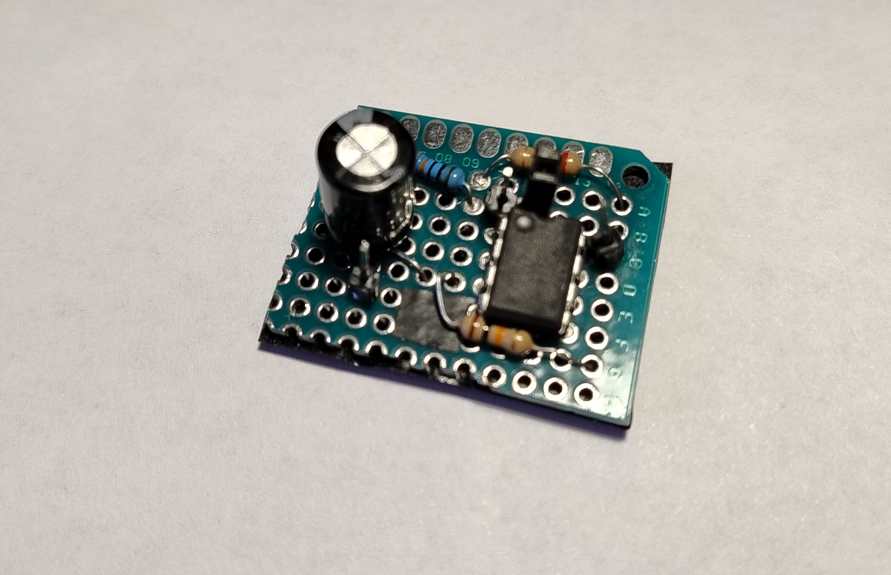
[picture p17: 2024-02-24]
images/reset_circuit.jpg

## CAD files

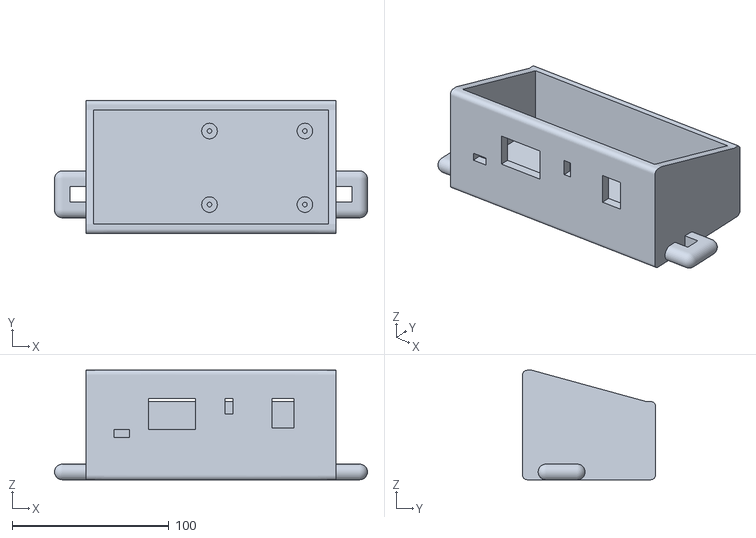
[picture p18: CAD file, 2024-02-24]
CASE/STL files/Structure_HEA.stl
200.0 x 85.0 x 70.0

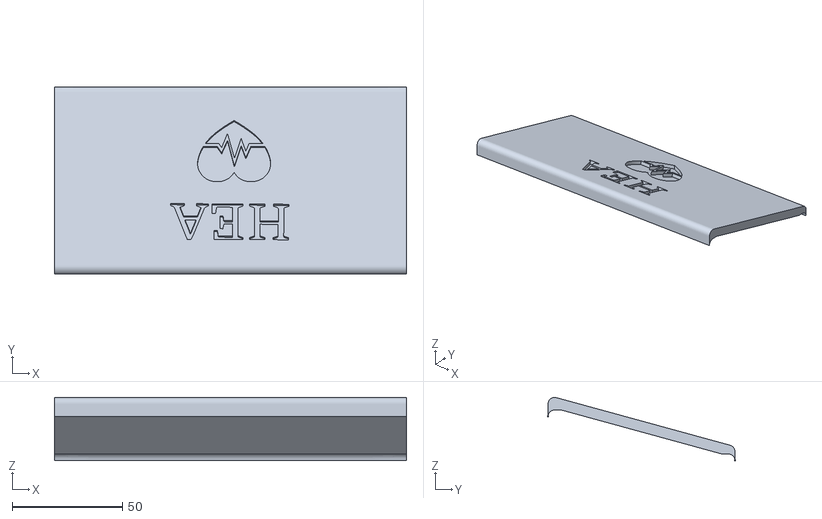
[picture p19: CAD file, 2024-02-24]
CASE/STL files/Lid_HEA.stl
160.0 x 85.0 x 28.7

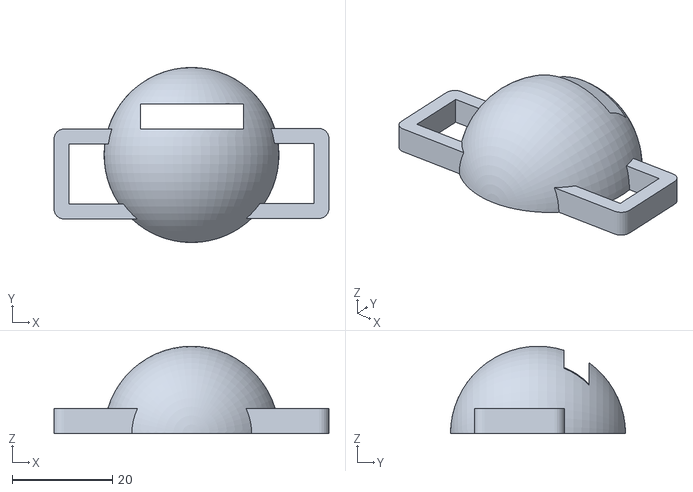
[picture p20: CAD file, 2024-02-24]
CASE/STL files/Shell2_HEA.stl
55.0 x 35.0 x 17.5

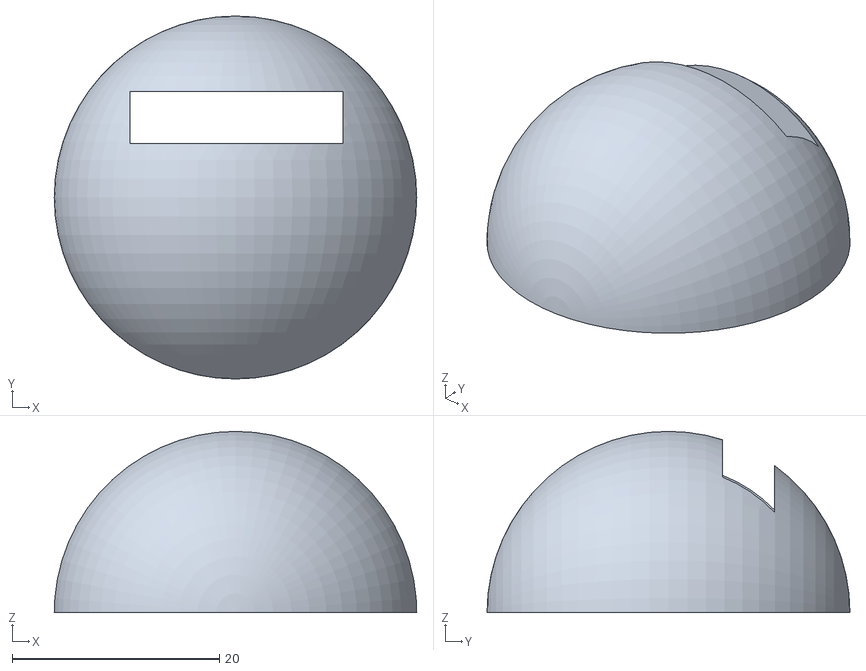
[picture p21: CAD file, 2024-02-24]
CASE/STL files/Shell1_HEA.stl
35.0 x 35.0 x 17.5

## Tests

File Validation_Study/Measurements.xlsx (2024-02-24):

Seated 1 |  |  |  |  |  |  |  |  |  |  | Standing 1 |  |  |  |  |  |  |  |  |  |  | Lying Down 1 |  |  |  |  |  |  |  |  |  |  | Seated 2 |  |  |  |  |  |  |  |  |  |  | Standing 2
HEA | Pulse Oximeter | P-H | mean error | mean abs error | max abs error | min abs error | SDAE | squared differences | RMSE | Statistica del test: 0.9809765373437471 | HEA | Pulse Oximeter | P-H |  |  |  |  | SDAE | squared differences | RMSE |  | HEA | Pulse Oximeter | P-H |  |  |  |  |  |  |  |  | HEA | Pulse Oximeter | P-H |  |  |  |  |  |  |  |  | HEA | Pulse Oximeter | P-H
65 | 62 | -3 | -2.37 | 3.63 | 8 | 0 | 2.316628515 | 9 | 4.3 | P-value: 0.15827375624701606 | 71 | 75 | 4 | mean error | mean abs error | max abs error | min abs error | 1.555017945 | 16 | 2.681417536 | Statistica del test: 0.9675534306331857 | 68 | 59 | -9 | mean error | mean abs error | max abs error | min abs error | SDAE | squared differences | RMSE | Statistica del test: 0.9747547948719316 | 55 | 60 | 5 | mean error | mean abs error | max abs error | min abs error | SDAE | squared differences | RMSE | Statistica del test: 0.9820380335783331 | 73 | 75 | 2 | mean error | mean abs error | max abs error | min abs error
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

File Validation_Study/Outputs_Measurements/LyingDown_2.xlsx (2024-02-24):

Acc totale
-8.6987
-8.6987
-8.6987
-8.6987
-8.7754
-8.6987
-8.737
-8.7754
-8.6604
-8.6987
-8.6987
-8.6987
-8.6987
-8.737
-8.737
-8.737
-8.6987
-8.7754
-8.737
-8.6987
-8.6604
-8.737
-8.6987
-8.6987
-8.6987
-8.6604
-8.5838
-8.6987
-8.7754
-8.6987
-8.737
-8.7754
-8.7754
-8.6604
-8.6987
-8.7754
-8.6221
-8.6987
-8.7754
-8.737
-8.7754
-8.6987
-8.6987
-8.6604
-8.6987
-8.7754
-8.737
-8.6987
-8.6987
-8.6987
-8.6987
-8.737
-8.6987
-8.6604
-8.737
-8.6987
-8.6987
-8.6987
-8.737
-8.6987
-8.737
-8.737
-8.6987
-8.737
-8.6987
-8.737
-8.6221
-8.7754
-8.737
-8.6987
-8.6221
-8.737
-8.737
-8.737
-8.737
-8.6604
-8.6987
-8.6604
-8.737
-8.737
-8.6987
-8.737
-8.6604
-8.8137
-8.6987
-8.6604
-8.6987
-8.6987
-8.7754
-8.7754
-8.6987
-8.6987
-8.737
-8.6987
-8.737
-8.737
-8.6987
-8.737
-8.6987
-8.6987
-8.6987
-8.6987
-8.6604
-8.737
-8.6987
-8.6604
-8.5454
-8.9286
-8.737
-8.5838
-8.6987
-8.737
-8.737
-8.737
-8.737
-8.737
-8.737
-8.6987
-8.6987
-8.6987
-8.737
-8.737
-8.737
-8.737
-8.6987
-8.737
-8.6604
-8.6987
-8.737
-8.7754
-8.6987
-8.6987
-8.6987
-8.6987
-8.737
-8.6987
-8.6987
-8.6987
-8.6987
-8.737
-8.6987
-8.6987
-8.6987
-8.737
-8.6987
-8.6987
-8.6987
-8.737
-8.7754
-8.737
-8.737
-8.6987
-8.6987
-8.6987
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

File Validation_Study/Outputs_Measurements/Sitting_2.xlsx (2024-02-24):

Acc totale
1.073
1.1496
1.1879
1.1879
1.073
1.1496
1.1113
1.1879
1.1496
1.073
1.1496
1.1496
1.1113
1.1496
1.073
1.1879
1.1496
1.1879
1.1113
1.1113
1.073
1.1879
1.1496
1.1496
1.1496
1.1496
1.073
1.1113
1.0346
1.073
1.2646
1.1879
1.1113
1.0346
1.0346
1.1879
1.1496
1.1113
1.1496
1.1113
1.1113
1.1879
1.1113
1.2646
1.2263
1.0346
1.1879
1.1113
1.1113
1.1496
1.1496
1.1113
1.1496
1.1496
1.1879
1.2263
1.1496
1.073
1.2263
1.1879
1.1496
1.1879
1.1879
1.1113
1.0346
1.1496
1.073
1.1496
1.073
1.1113
1.1879
1.1113
1.1879
1.1496
1.1879
1.1496
1.1113
1.1879
1.073
1.1113
1.1496
0.958
1.1113
1.1496
1.1113
1.1879
1.0346
1.1496
1.1879
1.2263
1.1113
1.1113
1.1113
1.0346
1.1496
1.073
1.073
1.1496
1.1879
1.1496
1.1113
1.0346
1.1879
1.1113
1.1879
1.1113
1.073
1.073
1.1113
1.1496
1.1496
1.1496
1.1113
1.2263
1.2263
1.1496
1.2263
1.1113
1.073
1.1496
1.1496
1.073
1.073
1.1496
1.1113
1.1879
1.1496
1.2263
1.1113
0.958
1.2646
1.2646
1.1113
1.1496
1.1496
1.073
1.073
1.1113
1.1496
1.1113
1.1113
1.1113
1.1879
1.073
1.1113
1.073
1.1879
1.1113
1.2263
1.073
1.1113
1.073
1.1113
1.1496
1.1879
1.3029
1.2263
1.1496
1.2263
1.1496
1.1496
1.1879
1.1879
1.2263
1.1113
1.1879
1.2263
1.1496
1.1879
1.1879
1.1113
1.1496
1.1496
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

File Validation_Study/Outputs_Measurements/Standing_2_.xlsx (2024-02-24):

Acc totale
2.4525
2.5675
2.5291
2.6441
2.4525
2.4525
2.4908
2.5675
2.5291
2.5291
2.5675
2.5291
2.4908
2.4525
2.5291
2.4525
2.5291
2.4525
2.5675
2.6058
2.4908
2.5291
2.4908
2.4908
2.5675
2.5291
2.5675
2.5291
2.5675
2.6058
2.5291
2.4908
2.3759
2.4908
2.4142
2.5675
2.5291
2.4908
2.4142
2.5291
2.4908
2.6058
2.5291
2.5291
2.6058
2.6058
2.5675
2.6441
2.4525
2.6058
2.5675
2.6058
2.5675
2.4908
2.5675
2.5675
2.4525
2.4908
2.5291
2.5291
2.5675
2.5675
2.5291
2.5291
2.5675
2.5675
2.5675
2.5291
2.5291
2.5675
2.6441
2.3759
2.5675
2.4908
2.6824
2.4525
2.4908
2.5675
2.4525
2.5291
2.5675
2.4525
2.5675
2.6058
2.5675
2.5291
2.6441
2.4525
2.5291
2.5675
2.5291
2.5291
2.5675
2.6058
2.5291
2.5675
2.5675
2.5675
2.4525
2.5291
2.5291
2.5675
2.4142
2.4908
2.5675
2.6058
2.4525
2.4142
2.5675
2.4525
2.4142
2.5675
2.4525
2.5291
2.4908
2.4525
2.5675
2.5291
2.5675
2.5291
2.4525
2.4908
2.4525
2.4908
2.4908
2.6058
2.4142
2.5291
2.5291
2.4908
2.4908
2.4525
2.5291
2.5675
2.4525
2.4908
2.5291
2.4908
2.4908
2.4908
2.4525
2.5291
2.5291
2.4142
2.5675
2.4908
2.4908
2.5291
2.4142
2.4525
2.4525
2.6058
2.5675
2.3375
2.4908
2.4142
2.5291
2.4908
2.5675
2.4908
2.5675
2.6058
2.5291
2.5291
2.4142
2.5291
2.4908
2.4908
2.5291
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

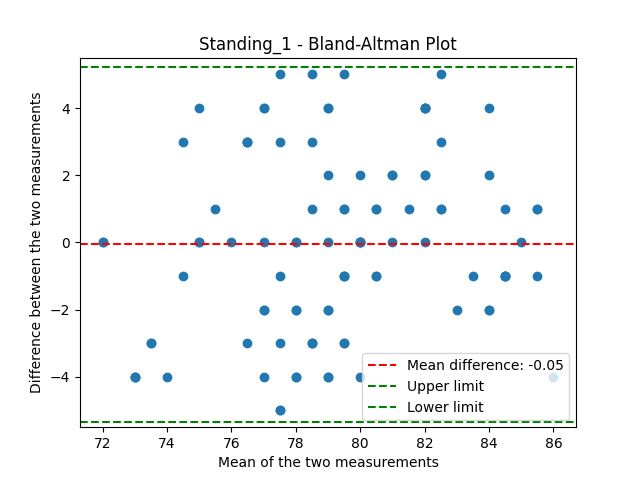
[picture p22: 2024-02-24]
Validation_Study/Plots/Standing_1_BA.png

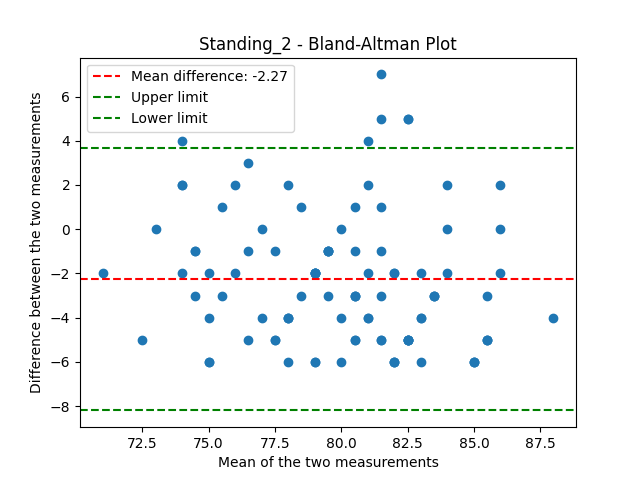
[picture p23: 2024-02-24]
Validation_Study/Plots/Standing_2_BA.png

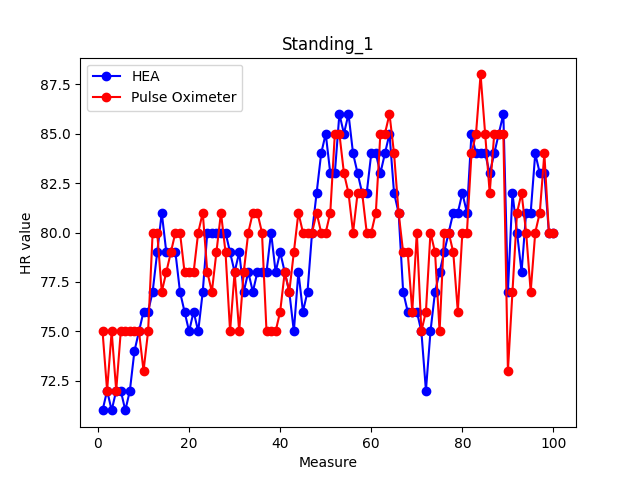
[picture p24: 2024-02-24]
Validation_Study/Plots/Standing_1.png

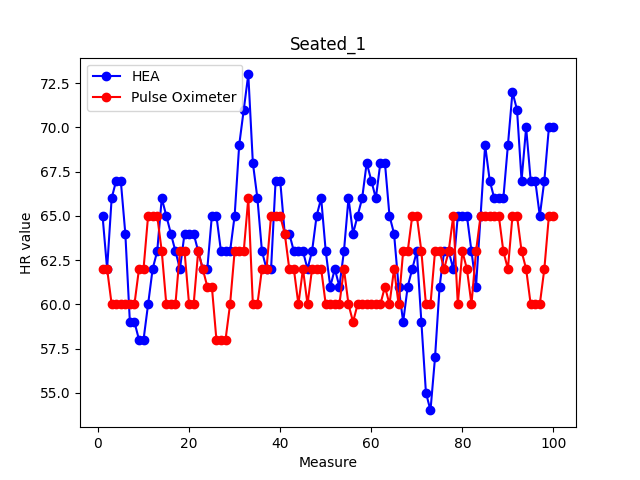
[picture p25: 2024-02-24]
Validation_Study/Plots/Seated_1.png

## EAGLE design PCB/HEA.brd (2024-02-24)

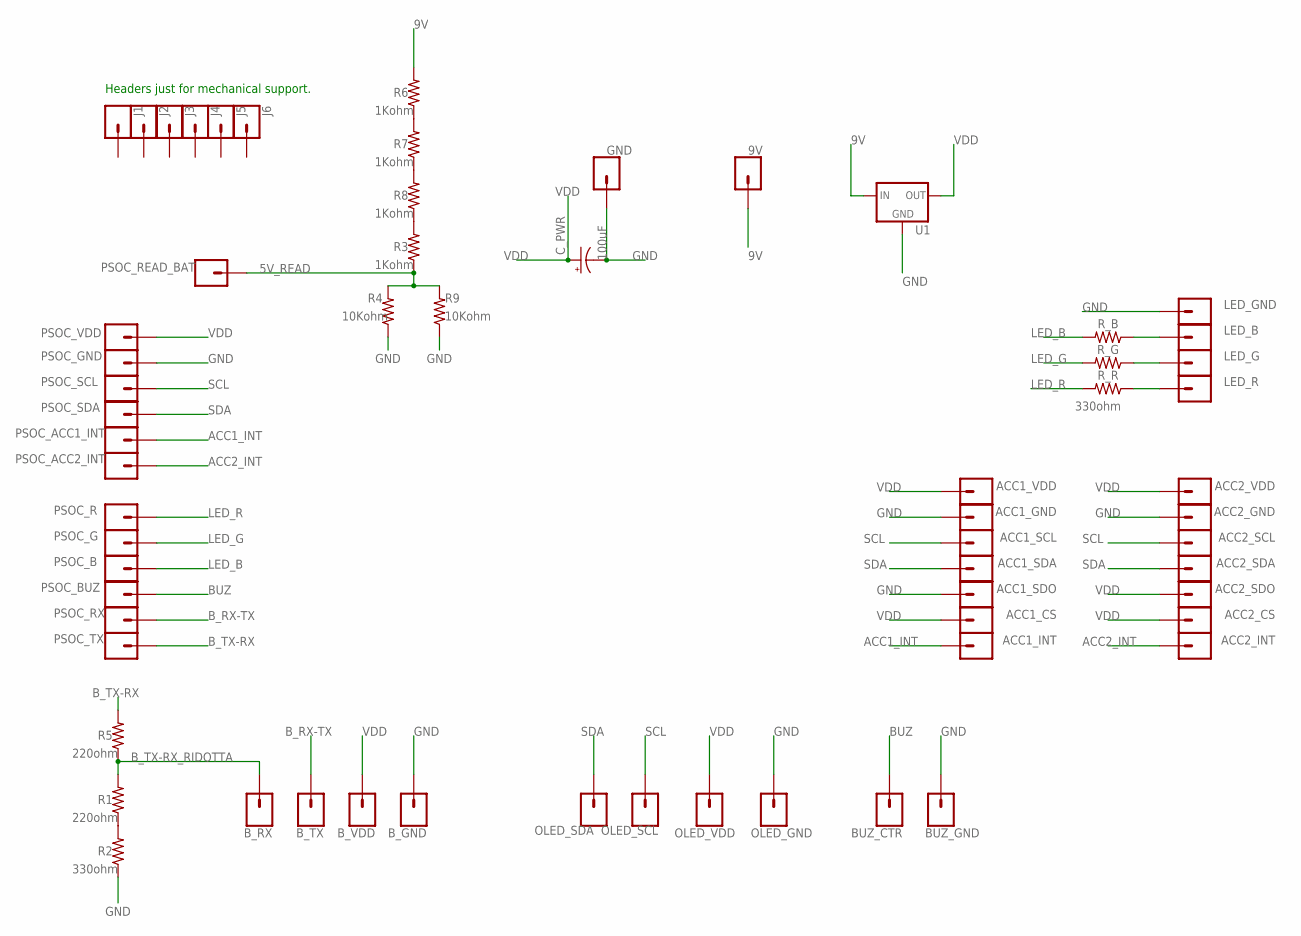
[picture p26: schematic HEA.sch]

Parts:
9V: CONN_01; 1X01
ACC1_CS, ACC1_GND, ACC1_INT, ACC1_SCL, ACC1_SDA, ACC1_SDO, ACC1_VDD, ACC2_CS, ACC2_GND, ACC2_INT, ACC2_SCL, ACC2_SDA, ACC2_SDO, ACC2_VDD: CONN_01; 1X01
BUZ_CTR: CONN_01; 1X01
BUZ_GND: CONN_01; 1X01
B_GND: CONN_01; 1X01
B_RX: CONN_01; 1X01
B_TX: CONN_01; 1X01
B_VDD: CONN_01; 1X01
C_PWR: 10uF; CPOL-RADIAL-2.5MM-5MM
GND: CONN_01; 1X01
J1, J2, J3, J4, J5, J6: CONN_01; 1X01
LED_B: CONN_01; 1X01
LED_G: CONN_01; 1X01
LED_GND: CONN_01; 1X01
LED_R: CONN_01; 1X01
OLED_GND: CONN_01; 1X01
OLED_SCL: CONN_01; 1X01
OLED_SDA: CONN_01; 1X01
OLED_VDD: CONN_01; 1X01
PSOC_ACC1_INT, PSOC_ACC2_INT: CONN_01; 1X01
PSOC_B: CONN_01; 1X01
PSOC_BUZ: CONN_01; 1X01
PSOC_G: CONN_01; 1X01
PSOC_GND: CONN_01; 1X01
PSOC_R: CONN_01; 1X01
PSOC_READ_BAT: CONN_01; 1X01
PSOC_RX: CONN_01; 1X01
PSOC_SCL: CONN_01; 1X01
PSOC_SDA: CONN_01; 1X01
PSOC_TX: CONN_01; 1X01
PSOC_VDD: CONN_01; 1X01
R1, R2, R3, R4, R5, R6, R7, R8, R9: AXIAL-0.3
R_B: AXIAL-0.3
R_G: AXIAL-0.3
R_R: AXIAL-0.3
U1: V_REG_78XX-TO-220; TO-220-ALT

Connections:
5V_READ: PSOC_READ_BAT.1, R3.P$1 (1), R4.P$2 (2), R9.P$2 (2)
9V: 9V.1, R6.P$2 (2), U1.IN
ACC1_INT: ACC1_INT.1, PSOC_ACC1_INT.1
ACC2_INT: ACC2_INT.1, PSOC_ACC2_INT.1
BUZ: BUZ_CTR.1, PSOC_BUZ.1
B_RX-TX: B_TX.1, PSOC_RX.1
B_TX-RX: PSOC_TX.1, R5.P$2 (2)
B_TX-RX_RIDOTTA: B_RX.1, R1.P$2 (2), R5.P$1 (1)
GND: ACC1_GND.1, ACC1_SDO.1, ACC2_GND.1, BUZ_GND.1, B_GND.1, C_PWR.2 (-), GND.1, LED_GND.1, OLED_GND.1, PSOC_GND.1, R2.P$1 (1), R4.P$1 (1), R9.P$1 (1), U1.GND
LED_B: PSOC_B.1, R_B.P$2 (2)
LED_G: PSOC_G.1, R_G.P$2 (2)
LED_R: PSOC_R.1, R_R.P$2 (2)
unnamed: R1.P$1 (1), R2.P$2 (2)
unnamed: R3.P$2 (2), R8.P$1 (1)
unnamed: LED_B.1, R_B.P$1 (1)
unnamed: LED_G.1, R_G.P$1 (1)
unnamed: LED_R.1, R_R.P$1 (1)
unnamed: R7.P$1 (1), R8.P$2 (2)
unnamed: R6.P$1 (1), R7.P$2 (2)
SCL: ACC1_SCL.1, ACC2_SCL.1, OLED_SCL.1, PSOC_SCL.1
SDA: ACC1_SDA.1, ACC2_SDA.1, OLED_SDA.1, PSOC_SDA.1
VDD: ACC1_CS.1, ACC1_VDD.1, ACC2_CS.1, ACC2_SDO.1, ACC2_VDD.1, B_VDD.1, C_PWR.1 (+), OLED_VDD.1, PSOC_VDD.1, U1.OUT

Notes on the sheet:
Headers just for mechanical support.

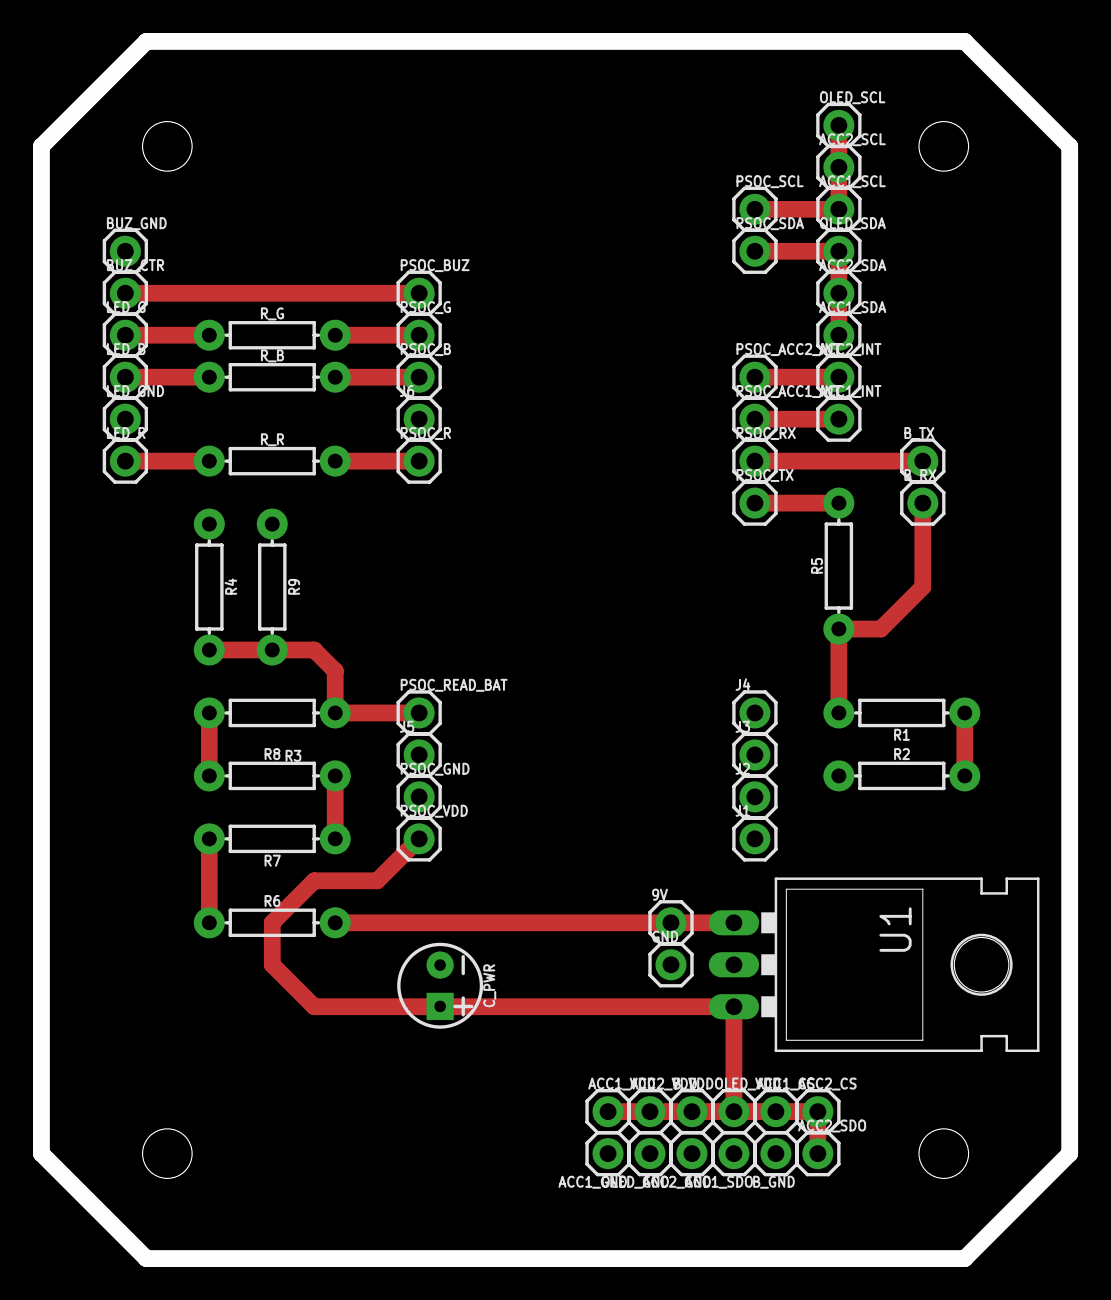
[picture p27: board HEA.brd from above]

Board: 2 copper layers, 62.2 x 73.7 mm, 63 parts (0 on the bottom side), 22 nets.

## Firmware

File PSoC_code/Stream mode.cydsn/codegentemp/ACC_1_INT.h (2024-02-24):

/*******************************************************************************
* File Name: ACC_1_INT.h  
* Version 2.20
*
* Description:
*  This file contains Pin function prototypes and register defines
*
* Note:
*
********************************************************************************
* Copyright 2008-2015, Cypress Semiconductor Corporation.  All rights reserved.
* You may use this file only in accordance with the license, terms, conditions, 
* disclaimers, and limitations in the end user license agreement accompanying 
* the software package with which this file was provided.
*******************************************************************************/

#if !defined(CY_PINS_ACC_1_INT_H) /* Pins ACC_1_INT_H */
#define CY_PINS_ACC_1_INT_H

#include "cytypes.h"
#include "cyfitter.h"
#include "cypins.h"
#include "ACC_1_INT_aliases.h"

/* APIs are not generated for P15[7:6] */
#if !(CY_PSOC5A &&\
	 ACC_1_INT__PORT == 15 && ((ACC_1_INT__MASK & 0xC0) != 0))


/***************************************
*        Function Prototypes             
***************************************/    

/**
* \addtogroup group_general
* @{
*/
void    ACC_1_INT_Write(uint8 value);
void    ACC_1_INT_SetDriveMode(uint8 mode);
uint8   ACC_1_INT_ReadDataReg(void);
uint8   ACC_1_INT_Read(void);
void    ACC_1_INT_SetInterruptMode(uint16 position, uint16 mode);
uint8   ACC_1_INT_ClearInterrupt(void);
/** @} general */

/***************************************
*           API Constants        
***************************************/
/**
* \addtogroup group_constants
* @{
*/
    /** \addtogroup driveMode Drive mode constants
     * \brief Constants to be passed as "mode" parameter in the ACC_1_INT_SetDriveMode() function.
     *  @{
     */
        #define ACC_1_INT_DM_ALG_HIZ         PIN_DM_ALG_HIZ
        #define ACC_1_INT_DM_DIG_HIZ         PIN_DM_DIG_HIZ
        #define ACC_1_INT_DM_RES_UP          PIN_DM_RES_UP
        #define ACC_1_INT_DM_RES_DWN         PIN_DM_RES_DWN
        #define ACC_1_INT_DM_OD_LO           PIN_DM_OD_LO
        #define ACC_1_INT_DM_OD_HI           PIN_DM_OD_HI
        #define ACC_1_INT_DM_STRONG          PIN_DM_STRONG
        #define ACC_1_INT_DM_RES_UPDWN       PIN_DM_RES_UPDWN
    /** @} driveMode */
/** @} group_constants */
    
/* Digital Port Constants */
#define ACC_1_INT_MASK               ACC_1_INT__MASK
#define ACC_1_INT_SHIFT              ACC_1_INT__SHIFT
#define ACC_1_INT_WIDTH              1u

/* Interrupt constants */
#if defined(ACC_1_INT__INTSTAT)
/**
* \addtogroup group_constants
* @{
*/
    /** \addtogroup intrMode Interrupt constants
     * \brief Constants to be passed as "mode" parameter in ACC_1_INT_SetInterruptMode() function.
     *  @{
     */
        #define ACC_1_INT_INTR_NONE      (uint16)(0x0000u)
        #define ACC_1_INT_INTR_RISING    (uint16)(0x0001u)
        #define ACC_1_INT_INTR_FALLING   (uint16)(0x0002u)
        #define ACC_1_INT_INTR_BOTH      (uint16)(0x0003u) 
    /** @} intrMode */
/** @} group_constants */

    #define ACC_1_INT_INTR_MASK      (0x01u) 
#endif /* (ACC_1_INT__INTSTAT) */


/***************************************
*             Registers        
***************************************/

/* Main Port Registers */
/* Pin State */
#define ACC_1_INT_PS                     (* (reg8 *) ACC_1_INT__PS)
/* Data Register */
#define ACC_1_INT_DR                     (* (reg8 *) ACC_1_INT__DR)
/* Port Number */
#define ACC_1_INT_PRT_NUM                (* (reg8 *) ACC_1_INT__PRT) 
/* Connect to Analog Globals */                                                  
#define ACC_1_INT_AG                     (* (reg8 *) ACC_1_INT__AG)                       
/* Analog MUX bux enable */
#define ACC_1_INT_AMUX                   (* (reg8 *) ACC_1_INT__AMUX) 
/* Bidirectional Enable */                                                        
#define ACC_1_INT_BIE                    (* (reg8 *) ACC_1_INT__BIE)
/* Bit-mask for Aliased Register Access */
#define ACC_1_INT_BIT_MASK               (* (reg8 *) ACC_1_INT__BIT_MASK)
/* Bypass Enable */
#define ACC_1_INT_BYP                    (* (reg8 *) ACC_1_INT__BYP)
/* Port wide control signals */                                                   
#define ACC_1_INT_CTL                    (* (reg8 *) ACC_1_INT__CTL)
/* Drive Modes */
#define ACC_1_INT_DM0                    (* (reg8 *) ACC_1_INT__DM0) 
#define ACC_1_INT_DM1                    (* (reg8 *) ACC_1_INT__DM1)
#define ACC_1_INT_DM2                    (* (reg8 *) ACC_1_INT__DM2) 
/* Input Buffer Disable Override */
#define ACC_1_INT_INP_DIS                (* (reg8 *) ACC_1_INT__INP_DIS)
/* LCD Common or Segment Drive */
#define ACC_1_INT_LCD_COM_SEG            (* (reg8 *) ACC_1_INT__LCD_COM_SEG)
/* Enable Segment LCD */
#define ACC_1_INT_LCD_EN                 (* (reg8 *) ACC_1_INT__LCD_EN)
/* Slew Rate Control */
#define ACC_1_INT_SLW                    (* (reg8 *) ACC_1_INT__SLW)

/* DSI Port Registers */
/* Global DSI Select Register */
#define ACC_1_INT_PRTDSI__CAPS_SEL       (* (reg8 *) ACC_1_INT__PRTDSI__CAPS_SEL) 
/* Double Sync Enable */
#define ACC_1_INT_PRTDSI__DBL_SYNC_IN    (* (reg8 *) ACC_1_INT__PRTDSI__DBL_SYNC_IN) 
/* Output Enable Select Drive Strength */
#define ACC_1_INT_PRTDSI__OE_SEL0        (* (reg8 *) ACC_1_INT__PRTDSI__OE_SEL0) 
#define ACC_1_INT_PRTDSI__OE_SEL1        (* (reg8 *) ACC_1_INT__PRTDSI__OE_SEL1) 
/* Port Pin Output Select Registers */
#define ACC_1_INT_PRTDSI__OUT_SEL0       (* (reg8 *) ACC_1_INT__PRTDSI__OUT_SEL0) 
#define ACC_1_INT_PRTDSI__OUT_SEL1       (* (reg8 *) ACC_1_INT__PRTDSI__OUT_SEL1) 
/* Sync Output Enable Registers */
#define ACC_1_INT_PRTDSI__SYNC_OUT       (* (reg8 *) ACC_1_INT__PRTDSI__SYNC_OUT) 

/* SIO registers */
#if defined(ACC_1_INT__SIO_CFG)
    #define ACC_1_INT_SIO_HYST_EN        (* (reg8 *) ACC_1_INT__SIO_HYST_EN)
    #define ACC_1_INT_SIO_REG_HIFREQ     (* (reg8 *) ACC_1_INT__SIO_REG_HIFREQ)
    #define ACC_1_INT_SIO_CFG            (* (reg8 *) ACC_1_INT__SIO_CFG)
    #define ACC_1_INT_SIO_DIFF           (* (reg8 *) ACC_1_INT__SIO_DIFF)
#endif /* (ACC_1_INT__SIO_CFG) */

/* Interrupt Registers */
#if defined(ACC_1_INT__INTSTAT)
    #define ACC_1_INT_INTSTAT            (* (reg8 *) ACC_1_INT__INTSTAT)
    #define ACC_1_INT_SNAP               (* (reg8 *) ACC_1_INT__SNAP)
    
	#define ACC_1_INT_0_INTTYPE_REG 		(* (reg8 *) ACC_1_INT__0__INTTYPE)
#endif /* (ACC_1_INT__INTSTAT) */

#endif /* CY_PSOC5A... */

#endif /*  CY_PINS_ACC_1_INT_H */


/* [] END OF FILE */

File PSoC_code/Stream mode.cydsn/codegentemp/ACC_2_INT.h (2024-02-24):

/*******************************************************************************
* File Name: ACC_2_INT.h  
* Version 2.20
*
* Description:
*  This file contains Pin function prototypes and register defines
*
* Note:
*
********************************************************************************
* Copyright 2008-2015, Cypress Semiconductor Corporation.  All rights reserved.
* You may use this file only in accordance with the license, terms, conditions, 
* disclaimers, and limitations in the end user license agreement accompanying 
* the software package with which this file was provided.
*******************************************************************************/

#if !defined(CY_PINS_ACC_2_INT_H) /* Pins ACC_2_INT_H */
#define CY_PINS_ACC_2_INT_H

#include "cytypes.h"
#include "cyfitter.h"
#include "cypins.h"
#include "ACC_2_INT_aliases.h"

/* APIs are not generated for P15[7:6] */
#if !(CY_PSOC5A &&\
	 ACC_2_INT__PORT == 15 && ((ACC_2_INT__MASK & 0xC0) != 0))


/***************************************
*        Function Prototypes             
***************************************/    

/**
* \addtogroup group_general
* @{
*/
void    ACC_2_INT_Write(uint8 value);
void    ACC_2_INT_SetDriveMode(uint8 mode);
uint8   ACC_2_INT_ReadDataReg(void);
uint8   ACC_2_INT_Read(void);
void    ACC_2_INT_SetInterruptMode(uint16 position, uint16 mode);
uint8   ACC_2_INT_ClearInterrupt(void);
/** @} general */

/***************************************
*           API Constants        
***************************************/
/**
* \addtogroup group_constants
* @{
*/
    /** \addtogroup driveMode Drive mode constants
     * \brief Constants to be passed as "mode" parameter in the ACC_2_INT_SetDriveMode() function.
     *  @{
     */
        #define ACC_2_INT_DM_ALG_HIZ         PIN_DM_ALG_HIZ
        #define ACC_2_INT_DM_DIG_HIZ         PIN_DM_DIG_HIZ
        #define ACC_2_INT_DM_RES_UP          PIN_DM_RES_UP
        #define ACC_2_INT_DM_RES_DWN         PIN_DM_RES_DWN
        #define ACC_2_INT_DM_OD_LO           PIN_DM_OD_LO
        #define ACC_2_INT_DM_OD_HI           PIN_DM_OD_HI
        #define ACC_2_INT_DM_STRONG          PIN_DM_STRONG
        #define ACC_2_INT_DM_RES_UPDWN       PIN_DM_RES_UPDWN
    /** @} driveMode */
/** @} group_constants */
    
/* Digital Port Constants */
#define ACC_2_INT_MASK               ACC_2_INT__MASK
#define ACC_2_INT_SHIFT              ACC_2_INT__SHIFT
#define ACC_2_INT_WIDTH              1u

/* Interrupt constants */
#if defined(ACC_2_INT__INTSTAT)
/**
* \addtogroup group_constants
* @{
*/
    /** \addtogroup intrMode Interrupt constants
     * \brief Constants to be passed as "mode" parameter in ACC_2_INT_SetInterruptMode() function.
     *  @{
     */
        #define ACC_2_INT_INTR_NONE      (uint16)(0x0000u)
        #define ACC_2_INT_INTR_RISING    (uint16)(0x0001u)
        #define ACC_2_INT_INTR_FALLING   (uint16)(0x0002u)
        #define ACC_2_INT_INTR_BOTH      (uint16)(0x0003u) 
    /** @} intrMode */
/** @} group_constants */

    #define ACC_2_INT_INTR_MASK      (0x01u) 
#endif /* (ACC_2_INT__INTSTAT) */


/***************************************
*             Registers        
***************************************/

/* Main Port Registers */
/* Pin State */
#define ACC_2_INT_PS                     (* (reg8 *) ACC_2_INT__PS)
/* Data Register */
#define ACC_2_INT_DR                     (* (reg8 *) ACC_2_INT__DR)
/* Port Number */
#define ACC_2_INT_PRT_NUM                (* (reg8 *) ACC_2_INT__PRT) 
/* Connect to Analog Globals */                                                  
#define ACC_2_INT_AG                     (* (reg8 *) ACC_2_INT__AG)                       
/* Analog MUX bux enable */
#define ACC_2_INT_AMUX                   (* (reg8 *) ACC_2_INT__AMUX) 
/* Bidirectional Enable */                                                        
#define ACC_2_INT_BIE                    (* (reg8 *) ACC_2_INT__BIE)
/* Bit-mask for Aliased Register Access */
#define ACC_2_INT_BIT_MASK               (* (reg8 *) ACC_2_INT__BIT_MASK)
/* Bypass Enable */
#define ACC_2_INT_BYP                    (* (reg8 *) ACC_2_INT__BYP)
/* Port wide control signals */                                                   
#define ACC_2_INT_CTL                    (* (reg8 *) ACC_2_INT__CTL)
/* Drive Modes */
#define ACC_2_INT_DM0                    (* (reg8 *) ACC_2_INT__DM0) 
#define ACC_2_INT_DM1                    (* (reg8 *) ACC_2_INT__DM1)
#define ACC_2_INT_DM2                    (* (reg8 *) ACC_2_INT__DM2) 
/* Input Buffer Disable Override */
#define ACC_2_INT_INP_DIS                (* (reg8 *) ACC_2_INT__INP_DIS)
/* LCD Common or Segment Drive */
#define ACC_2_INT_LCD_COM_SEG            (* (reg8 *) ACC_2_INT__LCD_COM_SEG)
/* Enable Segment LCD */
#define ACC_2_INT_LCD_EN                 (* (reg8 *) ACC_2_INT__LCD_EN)
/* Slew Rate Control */
#define ACC_2_INT_SLW                    (* (reg8 *) ACC_2_INT__SLW)

/* DSI Port Registers */
/* Global DSI Select Register */
#define ACC_2_INT_PRTDSI__CAPS_SEL       (* (reg8 *) ACC_2_INT__PRTDSI__CAPS_SEL) 
/* Double Sync Enable */
#define ACC_2_INT_PRTDSI__DBL_SYNC_IN    (* (reg8 *) ACC_2_INT__PRTDSI__DBL_SYNC_IN) 
/* Output Enable Select Drive Strength */
#define ACC_2_INT_PRTDSI__OE_SEL0        (* (reg8 *) ACC_2_INT__PRTDSI__OE_SEL0) 
#define ACC_2_INT_PRTDSI__OE_SEL1        (* (reg8 *) ACC_2_INT__PRTDSI__OE_SEL1) 
/* Port Pin Output Select Registers */
#define ACC_2_INT_PRTDSI__OUT_SEL0       (* (reg8 *) ACC_2_INT__PRTDSI__OUT_SEL0) 
#define ACC_2_INT_PRTDSI__OUT_SEL1       (* (reg8 *) ACC_2_INT__PRTDSI__OUT_SEL1) 
/* Sync Output Enable Registers */
#define ACC_2_INT_PRTDSI__SYNC_OUT       (* (reg8 *) ACC_2_INT__PRTDSI__SYNC_OUT) 

/* SIO registers */
#if defined(ACC_2_INT__SIO_CFG)
    #define ACC_2_INT_SIO_HYST_EN        (* (reg8 *) ACC_2_INT__SIO_HYST_EN)
    #define ACC_2_INT_SIO_REG_HIFREQ     (* (reg8 *) ACC_2_INT__SIO_REG_HIFREQ)
    #define ACC_2_INT_SIO_CFG            (* (reg8 *) ACC_2_INT__SIO_CFG)
    #define ACC_2_INT_SIO_DIFF           (* (reg8 *) ACC_2_INT__SIO_DIFF)
#endif /* (ACC_2_INT__SIO_CFG) */

/* Interrupt Registers */
#if defined(ACC_2_INT__INTSTAT)
    #define ACC_2_INT_INTSTAT            (* (reg8 *) ACC_2_INT__INTSTAT)
    #define ACC_2_INT_SNAP               (* (reg8 *) ACC_2_INT__SNAP)
    
	#define ACC_2_INT_0_INTTYPE_REG 		(* (reg8 *) ACC_2_INT__0__INTTYPE)
#endif /* (ACC_2_INT__INTSTAT) */

#endif /* CY_PSOC5A... */

#endif /*  CY_PINS_ACC_2_INT_H */


/* [] END OF FILE */

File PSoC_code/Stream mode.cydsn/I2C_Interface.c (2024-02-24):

/* ========================================
 *
 * Politecnico di Milano 
 * LTEBS A.Y. 2023/24 
 * Mentasti, Pettenella, Salama, Vacca
 *
 * ========================================
*/

/*
* This file includes all the required source code to interface
* the I2C peripheral.
*/

/**
*   \brief Value returned if device present on I2C bus.
*/
#ifndef DEVICE_CONNECTED
    #define DEVICE_CONNECTED 1
#endif

/**
*   \brief Value returned if device not present on I2C bus.
*/
#ifndef DEVICE_UNCONNECTED
    #define DEVICE_UNCONNECTED 0
#endif

#include "I2C_Interface.h" 
#include "I2C_Master.h"

ErrorCode I2C_Peripheral_Start(void) 
{
    // Start I2C peripheral
    I2C_Master_Start();  
    
    // Return no error since start function does not return any error
    return NO_ERROR;
}

// --------------------------------------------------------------------------------- //

ErrorCode I2C_Peripheral_Stop(void)
{
    // Stop I2C peripheral
    I2C_Master_Stop();
    // Return no error since stop function does not return any error
    return NO_ERROR;
}
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

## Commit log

2024-02-24 add CAD
    [Clip_HEA.stl, Lid_HEA.stl, Shell1_HEA.stl, Shell2_HEA.stl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]
2024-02-24 add PCB
    [HEA.brd, HEA.sch]
2024-02-24 add Validation study
    [LyingDown_2.xlsx, Measurements.xlsx, Sitting_2.xlsx, Standing_2_.xlsx]

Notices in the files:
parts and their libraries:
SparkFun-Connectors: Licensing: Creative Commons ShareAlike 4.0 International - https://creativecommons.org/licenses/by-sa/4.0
